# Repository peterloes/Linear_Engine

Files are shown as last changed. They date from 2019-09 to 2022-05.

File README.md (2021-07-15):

# Linear Actuator

A standalone Platform for Animal Manipulation 

This is the firmware for the LinearA_2017 (linear servo, i.e. stepper motor with spindle)
and project Servo_2015 (standard PWM servo).
Setup and control of the Actuator is done
via 3 keys, and, for selecting the two end positions, also via two external
inputs, please see below.  The firmware supports soft-start, i.e. the Actuator
speed will be ramped-up during the start phase.

Supported:
- Nanotec SMC11-2 Leistungsendstufe
- Nanotec Linear Aktuator L2018S0604-T3,5x1

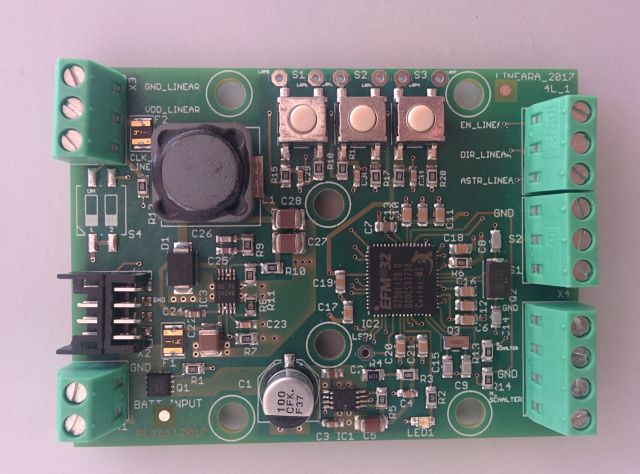
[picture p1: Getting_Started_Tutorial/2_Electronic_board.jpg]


The linear setup procedure consists of 4 steps:
- Adjust end position 1.  A linear actuator
  doesn't know about its absolute position, therefore it first moves to
  to its physical start position (near the motor) after power-up.  From
  that, position 1 can be adjusted.
- Adjust end position 2.  This is the opposite end position to position 1.
- Adjust actuator speed.  The actuator permanently moves between the two end
  points.  The speed can be adjusted via S1 and S2.
- Asserting S3 the 4th time stores the servo parameters into FLASH and
  returns to normal operation.

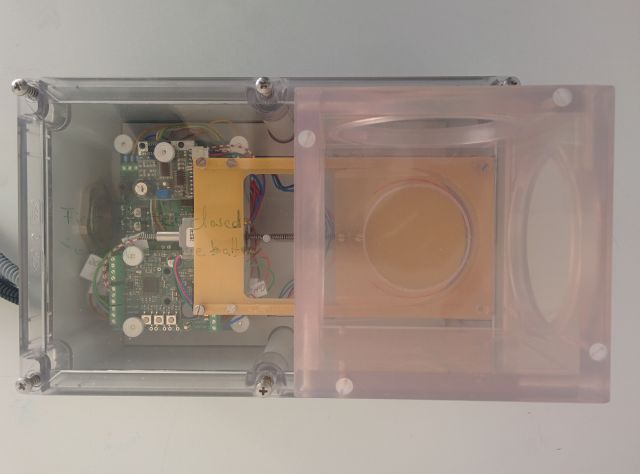
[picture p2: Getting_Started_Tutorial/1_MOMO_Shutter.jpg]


Prototype: Feeder

https://github.com/peterloes/Linear_Engine/blob/master/Getting_Started_Tutorial/1_poster_overview.pdf

Mainboard:

https://github.com/peterloes/MOMO

Manufacture:

https://github.com/peterloes/Linear_Engine/blob/master/Getting_Started_Tutorial/3_Supplier.txt

The standalone Linear Actuator features EFM32 ...the world´s most energy friendly microcontrollers

ARM Cortex-M3 EFM32G230F128

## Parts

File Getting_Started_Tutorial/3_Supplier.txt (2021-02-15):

Linear Actuator & Power Output Stage

L2018S0604-T3,5X1 Linearaktuator 
SMC11-2 Mikroschritt Leistungsendstufe
ZK-SMC11 Anschlusskabel
ZST3,5-1200-1 

Nanotec Electronic GmbH & Co. KG
Kapellenstr. 6
D-85622 Feldkirchen b. München 

Telefon: ++49-89-900686-0
Fax:     ++49-89-900686-50
Email:   info@nanotec.de
http://www.nanotec.de

Supplier of all Electronic Boards

Top-Print Electronic GmbH
Oskar Schmid

Rosenheimer Landstr. 129a
85521 Ottobrunn
Germany
Tel.: +49-89-60668047
Fax: +49-89-60668049
mailto: info@top-print.eu
https://www.leiterplatten-muenchen.de/

Protective coating with Schmelzharz Bectron MR3404

KC – Kunststoff- Chemische Produkte GmbH
Holger Sarau-Burghardt

Leonberger Straße 86 
DE 71292 Friolzheim
phone: +49 (0)7044 9425 13
e-mail: h.sarau-burghardt@kc-produkte.com
http: www.conformalcoating.de

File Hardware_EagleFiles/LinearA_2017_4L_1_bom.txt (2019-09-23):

Part  Value                Device                  Package                Description                                                    MF MPN OC_FARNELL OC_NEWARK
C1    100µ/16V             CPOL-EUE                PANASONIC_E            POLARIZED CAPACITOR, European symbol                                                      
C2    1uF                  C-EUC0603               C0603                  CAPACITOR, European symbol                                                                
C3    1nF                  C-EUC0603               C0603                  CAPACITOR, European symbol                                                                
C4    10nF                 C-EUC0603               C0603                  CAPACITOR, European symbol                                                                
C5    10uF                 C-EUC1206               C1206                  CAPACITOR, European symbol                                                                
C6    100n                 C_SMD0805               0805                                                                                                             
C7    1u                   C_SMD0805               0805                                                                                                             
C8    12p                  C_SMD0805               0805                                                                                                             
C9    18p                  C_SMD0805               0805                                                                                                             
C10   100n                 C_SMD0805               0805                                                                                                             
C11   100n                 C_SMD0805               0805                                                                                                             
C12   100n                 C_SMD0805               0805                                                                                                             
C13   100n                 C_SMD0805               0805                                                                                                             
C14   12p                  C_SMD0805               0805                                                                                                             
C15   18p                  C_SMD0805               0805                                                                                                             
C16   100n                 C_SMD0805               0805                                                                                                             
C17   100n                 C_SMD0805               0805                                                                                                             
C18   100n                 C_SMD0805               0805                                                                                                             
C19   100n                 C_SMD0805               0805                                                                                                             
C20   100n                 C_SMD0805               0805                                                                                                             
C21   100n                 C_SMD0805               0805                                                                                                             
C22   4.7µF                C-EUC1210               C1210                  CAPACITOR, European symbol                                                                
C23   10nF                 C-EUC0603               C0603                  CAPACITOR, European symbol                                                                
C24   100nF                C-EUC0603               C0603                  CAPACITOR, European symbol                                                                
C25   4.3nF                C-EUC0603               C0603                  CAPACITOR, European symbol                                                                
C26   24pF                 C-EUC0603               C0603                  CAPACITOR, European symbol                                                                
C27   22µF                 C-EUC1210               C1210                  CAPACITOR, European symbol                                                                
C28   22µF                 C-EUC1210               C1210                  CAPACITOR, European symbol                                                                
C29   10n                  C-EUC0603               C0603                  CAPACITOR, European symbol                                                                
C30   10n                  C-EUC0603               C0603                  CAPACITOR, European symbol                                                                
C31   10n                  C-EUC0603               C0603                  CAPACITOR, European symbol                                                                
D1    B360B                SCHOTTKY-DIODESMD       SMB                    Schottky Diode                                                                            
F1    MF-USMF050           PFUF                    PFUF_1210POLY                                                                                                    
F2    MF-USMF050           PFUF                    PFUF_1210POLY                                                                                                    
IC1   TPS7A1601DGNT        TPS7A16                 DGN_S-PDSO-G8-EXP                                                                                                
IC2   EFM32G230F128        EFM32G230F128           QFN64                  EFM32G230F128 Gecko Microcontroller in 9mm x 9mm QFN64 package                            
IC3   TPS54240DGQR         TPS54240DGQR            S-PDSO-G10                                                                                                       
L1    PIS4728-220M-04      DR127                   DR127                  High Power Density, High Efficiency, Shielded Inductors                                   
LED1  SML-H12U8TT86        LEDCHIPLED_0805         CHIPLED_0805           LED                                                                                       
LSP1  (n.b.)LSP10          LSP10                   LSP10                  SOLDER PAD drill 1.0 mm, distributor Buerklin, 12H555                                     
LSP2  (n.b.)LSP10          LSP10                   LSP10                  SOLDER PAD drill 1.0 mm, distributor Buerklin, 12H555                                     
LSP3  (n.b.)LSP10          LSP10                   LSP10                  SOLDER PAD drill 1.0 mm, distributor Buerklin, 12H555                                     
LSP4  (n.b.)LSP10          LSP10                   LSP10                  SOLDER PAD drill 1.0 mm, distributor Buerklin, 12H555                                     
LSP5  (n.b.)LSP10          LSP10                   LSP10                  SOLDER PAD drill 1.0 mm, distributor Buerklin, 12H555                                     
LSP6  (n.b.)LSP10          LSP10                   LSP10                  SOLDER PAD drill 1.0 mm, distributor Buerklin, 12H555                                     
LSP7  (n.b.)LSP10          LSP10                   LSP10                  SOLDER PAD drill 1.0 mm, distributor Buerklin, 12H555                                     
PASS1 ROUND_1MM1.5         ROUND_1MM1.5            ROUND2_1.5MM                                                                                                     
PASS2 ROUND_1MM1.5         ROUND_1MM1.5            ROUND2_1.5MM                                                                                                     
Q1    SI7121DN             TRANSISTOR-FET_SI7113DN TRANSISTOR-FET_1212-8S                                                                                           
Q2    NX5032GA/32MHz/8pF   CRYSTAL2P5.0X3.2        CRYSTAL2P5.0X3.2       Quarz Crystal                                                                             
Q3    CM7V, 32768Hz/12.5pF CRYSTAL2P               CRYSTAL2P3.2X1.5       Quarz Crystal                                                                             
R1    100k                 R-EU_R0805              R0805                  RESISTOR, European symbol                                                                 
R2    1K2                  R-EU_R0805              R0805                  RESISTOR, European symbol                                                                 
R3    2M                   R-EU_R0805              R0805                  RESISTOR, European symbol                                                                 
R4    1M13                 R-EU_R0805              R0805                  RESISTOR, European symbol                                                                 
R5    100K                 R-EU_R0805              R0805                  RESISTOR, European symbol                                                                 
R6    1                    R-EU_R0805              R0805                  RESISTOR, European symbol                                                                 
R7    100K                 R-EU_R0805              R0805                  RESISTOR, European symbol                                                                 
R8    348K                 R-EU_R0805              R0805                  RESISTOR, European symbol                                                                 
R9    39K                  R-EU_R0805              R0805                  RESISTOR, European symbol                                                                 
R10   140K                 R-EU_R0805              R0805                  RESISTOR, European symbol                                                                 
R11   10k                  R-EU_R0805              R0805                  RESISTOR, European symbol                                                                 
R12   100                  R-EU_R0805              R0805                  RESISTOR, European symbol                                                                 
R13   1K                   R-EU_R0805              R0805                  RESISTOR, European symbol                                                                 
R14   1K                   R-EU_R0805              R0805                  RESISTOR, European symbol                                                                 
R15   100K                 R-EU_R0805              R0805                  RESISTOR, European symbol                                                                 
R16   100K                 R-EU_R0805              R0805                  RESISTOR, European symbol                                                                 
R17   100K                 R-EU_R0805              R0805                  RESISTOR, European symbol                                                                 
R18   100                  R-EU_R0805              R0805                  RESISTOR, European symbol                                                                 
R19   100                  R-EU_R0805              R0805                  RESISTOR, European symbol                                                                 
R20   100                  R-EU_R0805              R0805                  RESISTOR, European symbol                                                                 
S1    SWPB_B3S1000         DTSM-6                  DTSM-6                                                                                                           
S2    SWPB_B3S1000         DTSM-6                  DTSM-6                                                                                                           
S3    SWPB_B3S1000         DTSM-6                  DTSM-6                                                                                                           
S4    (n.b.)SBS9102TK      219-02                  CTS-219-02             Surface Mount DIP Switch Series 219 SMT                               unknown    unknown  
X1    MKDS1/2-3,81         MKDS1/2-3,81            2POL381                MKDS 1/2-3,81 - Order No. 1727010 (RS-Online - 101-5384)                                  
X2    DP11_8DP_2DS         DP11_8DP_2DS            DP11_8DP-2DS                                                                                                     
X3    MKDS1/3-3,81         MKDS1/3-3,81            3POL381                MKDS 1/3-3,81 - Order No. 1727023 (RS-Online - 101-5390)                                  
X4    MKDS1/3-3,81         MKDS1/3-3,81            3POL381                MKDS 1/3-3,81 - Order No. 1727023 (RS-Online - 101-5390)                                  
X5    MKDS1/3-3,81         MKDS1/3-3,81            3POL381                MKDS 1/3-3,81 - Order No. 1727023 (RS-Online - 101-5390)                                  
X6    MKDS1/4-3,81         MKDS1/4-3,81            4POL381                MKDS 1/4-3,81 - Order No. 1727036

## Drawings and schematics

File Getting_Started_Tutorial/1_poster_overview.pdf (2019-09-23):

# Linear actuator and servomotor

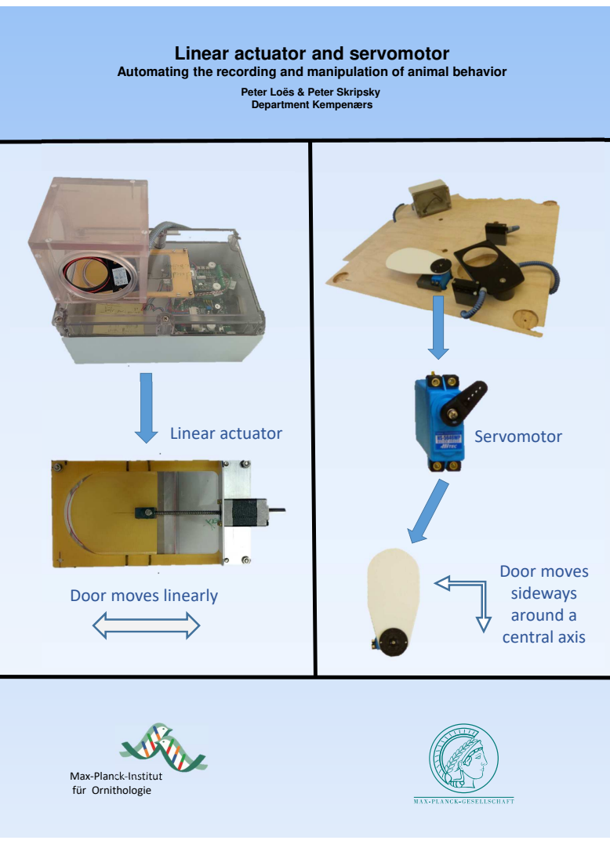
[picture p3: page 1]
Servomotor; Door moves sideways around a central axis; Linear actuator

Automating the recording and manipulation of animal behavior

Peter Loës & Peter Skripsky
Department Kempenærs

Door moves linearly

Max-Planck-Institut
für Ornithologie

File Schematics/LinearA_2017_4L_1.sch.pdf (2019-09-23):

### Wide Input Voltage Range: 12V to 35V VDD_LINEAR 9V - max. 35V

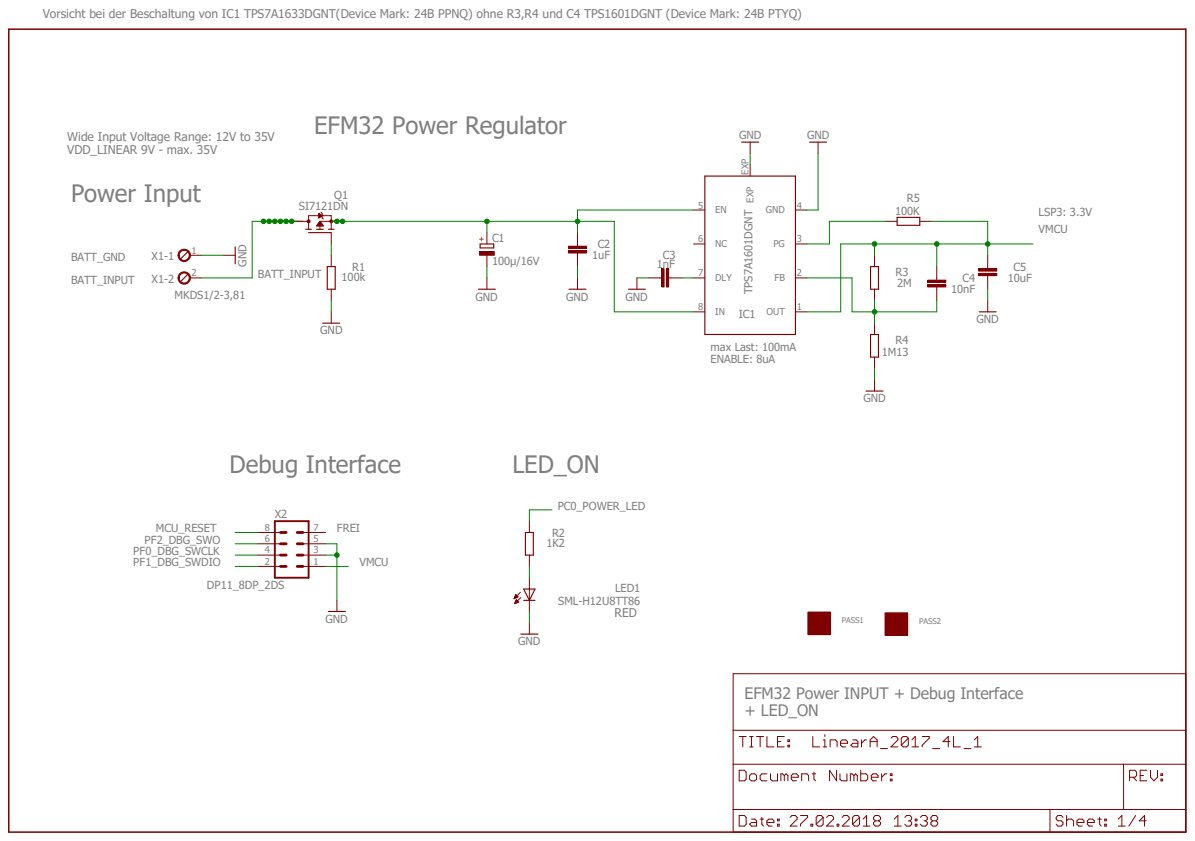
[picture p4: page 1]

Vorsicht bei der Beschaltung von IC1 TPS7A1633DGNT(Device Mark: 24B PPNQ) ohne R3,R4 und C4 TPS1601DGNT (Device Mark: 24B PTYQ)

EFM32 Power INPUT + Debug Interface
+ LED_ON

# EFM32 I/O + POWER

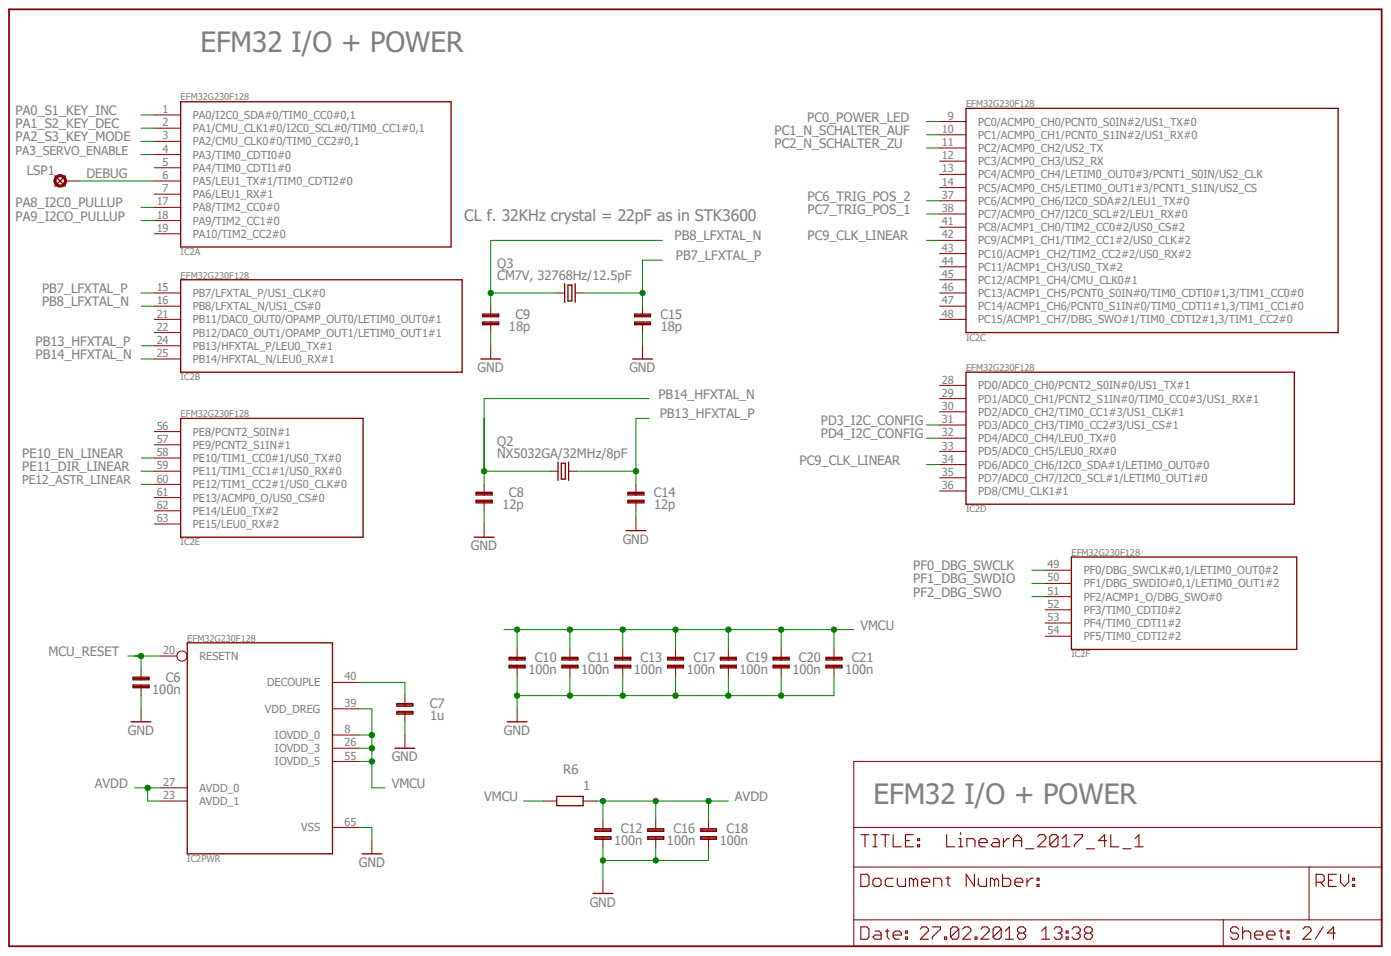
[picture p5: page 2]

CL f. 32KHz crystal = 22pF as in STK3600

## 11V_Ausgabe

# POWER OUTPUTs

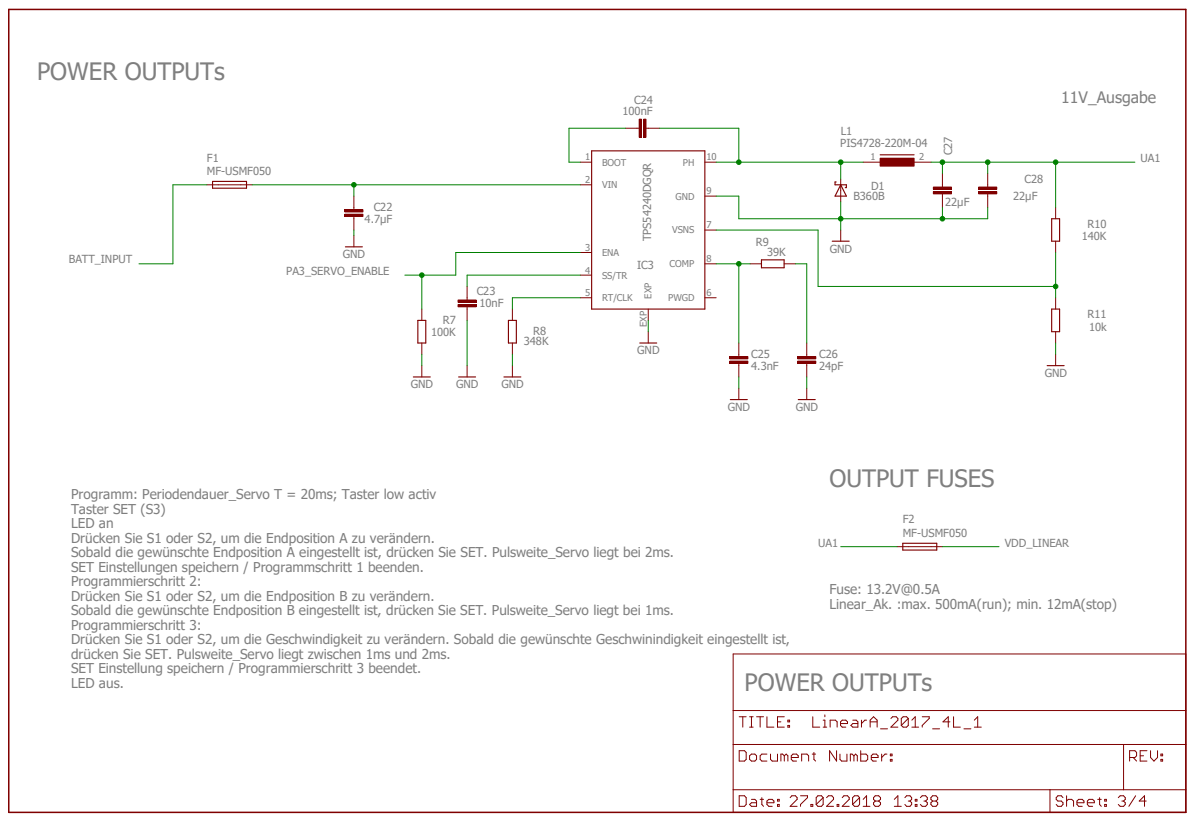
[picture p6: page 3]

Programm: Periodendauer_Servo T = 20ms; Taster low activ
Taster SET (S3)
LED an
Drücken Sie S1 oder S2, um die Endposition A zu verändern.
Sobald die gewünschte Endposition A eingestellt ist, drücken Sie SET. Pulsweite_Servo liegt bei 2ms.
SET Einstellungen speichern / Programmschritt 1 beenden.
Programmierschritt 2:
Drücken Sie S1 oder S2, um die Endposition B zu verändern.
Sobald die gewünschte Endposition B eingestellt ist, drücken Sie SET. Pulsweite_Servo liegt bei 1ms.
Programmierschritt 3:
Drücken Sie S1 oder S2, um die Geschwindigkeit zu verändern. Sobald die gewünschte Geschwinindigkeit eingestellt ist,
drücken Sie SET. Pulsweite_Servo liegt zwischen 1ms und 2ms.
SET Einstellung speichern / Programmierschritt 3 beendet.
LED aus.

Fuse: 13.2V@0.5A
Linear_Ak. :max. 500mA(run); min. 12mA(stop)

# LINEAR

## SMC11_Nanotec

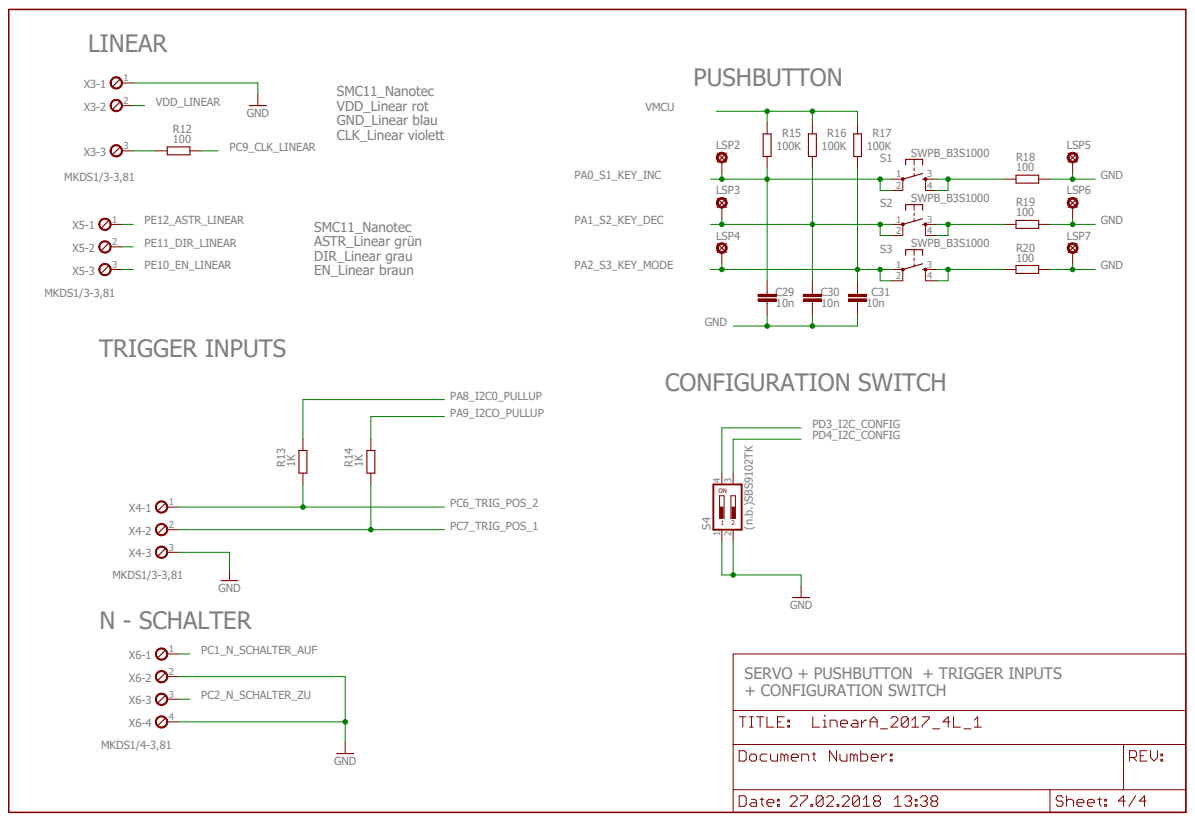
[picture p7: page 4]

SERVO + PUSHBUTTON + TRIGGER INPUTS
+ CONFIGURATION SWITCH

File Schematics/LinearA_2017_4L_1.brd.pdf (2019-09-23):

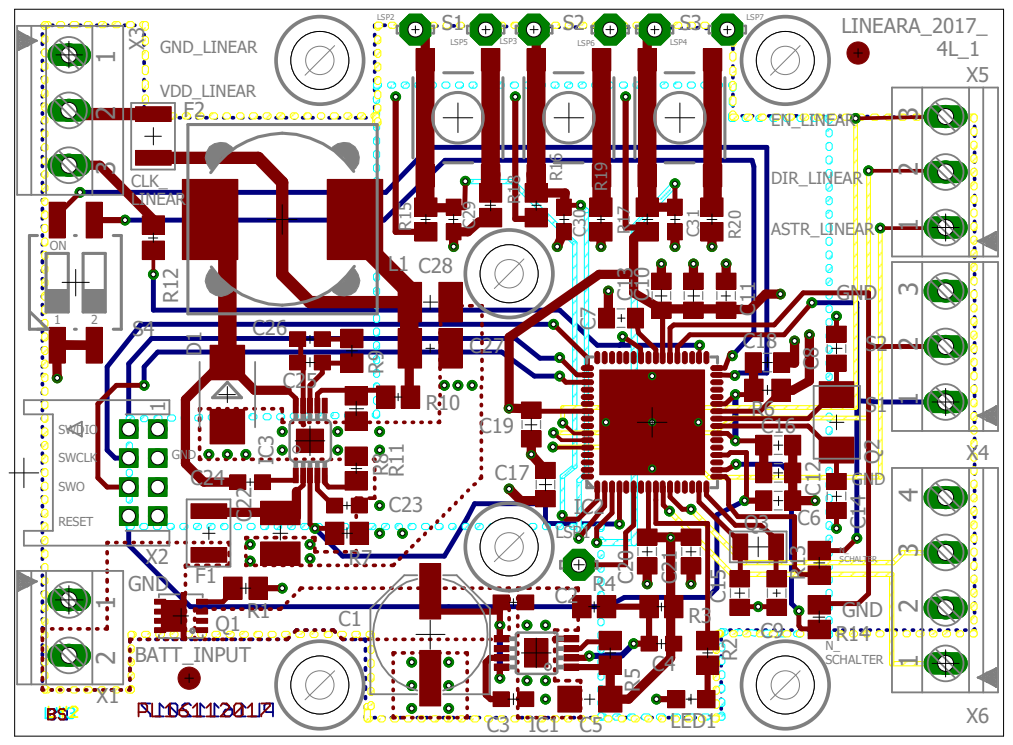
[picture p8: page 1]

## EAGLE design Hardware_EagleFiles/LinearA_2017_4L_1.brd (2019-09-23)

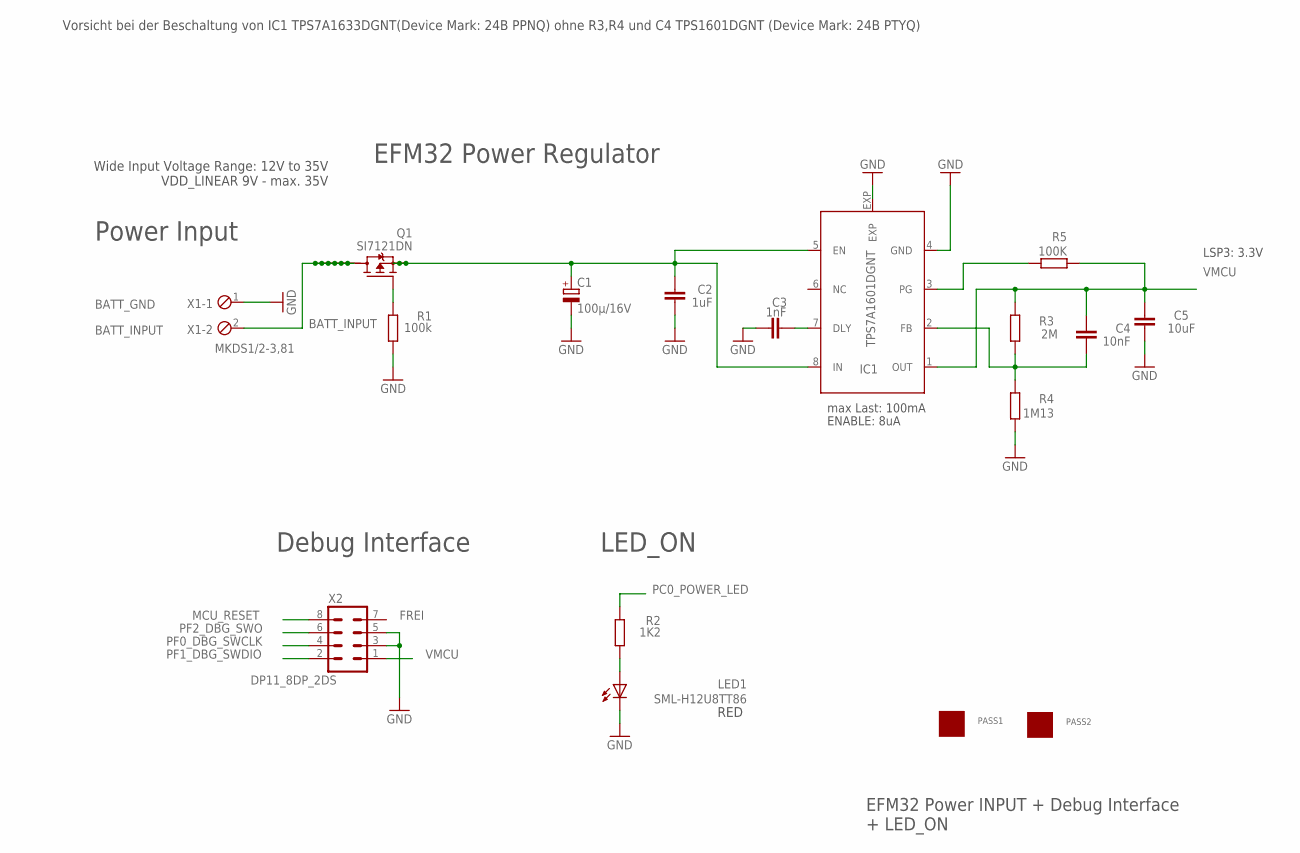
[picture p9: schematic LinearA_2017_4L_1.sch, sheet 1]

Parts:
C1: 100µ/16V; PANASONIC_E
C2: 1uF; C0603
C3: 1nF; C0603
C4: 10nF; C0603
C5: 10uF; C1206
IC1: TPS7A1601DGNT; DGN_S-PDSO-G8-EXP
LED1: SML-H12U8TT86; CHIPLED_0805
PASS1, PASS2: ROUND_1MM1.5; ROUND2_1.5MM
Q1: SI7121DN; TRANSISTOR-FET_1212-8S
R1: 100k; R0805
R2: 1K2; R0805
R3: 2M; R0805
R4: 1M13; R0805
R5: 100K; R0805
X1: MKDS1/2-3,81; 2POL381
X2: DP11_8DP_2DS; DP11_8DP-2DS

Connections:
BATT_INPUT: Q1.5 (D), Q1.6 (D), Q1.7 (D), Q1.8 (D), Q1.9 (D), Q1.10 (D), Q1.11 (D), X1.2; also elsewhere on the board
GND: C1.-, C2.1, C3.1, C5.1, IC1.4 (GND), IC1.EXP, LED1.C, R1.1, R4.1, X1.1, X2.3, X2.5; also elsewhere on the board
MCU_RESET: X2.8; also elsewhere on the board
unnamed: C1.+, C2.2, IC1.5 (EN), IC1.8 (IN), Q1.1 (S), Q1.2 (S), Q1.3 (S)
unnamed: C3.2, IC1.7 (DLY)
unnamed: C4.1, IC1.2 (FB), R3.1, R4.2
unnamed: IC1.3 (PG), R5.2
unnamed: Q1.4 (G), R1.2
unnamed: LED1.A, R2.2
PC0_POWER_LED: R2.1; also elsewhere on the board
PF0_DBG_SWCLK: X2.4; also elsewhere on the board
PF1_DBG_SWDIO: X2.2; also elsewhere on the board
PF2_DBG_SWO: X2.6; also elsewhere on the board
VMCU: C4.2, C5.2, IC1.1 (OUT), R3.2, R5.1, X2.1; also elsewhere on the board

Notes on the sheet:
BATT_GND
Wide Input Voltage Range: 12V to 35V VDD_LINEAR 9V - max. 35V
BATT_INPUT
EFM32 Power INPUT + Debug Interface + LED_ON
ENABLE: 8uA
Power Input
max Last: 100mA
LSP3: 3.3V
EFM32 Power Regulator
Debug Interface
LED_ON
FREI
Vorsicht bei der Beschaltung von IC1 TPS7A1633DGNT(Device Mark: 24B PPNQ) ohne R3,R4 und C4 TPS1601DGNT (Device Mark: 24B PTYQ)
RED

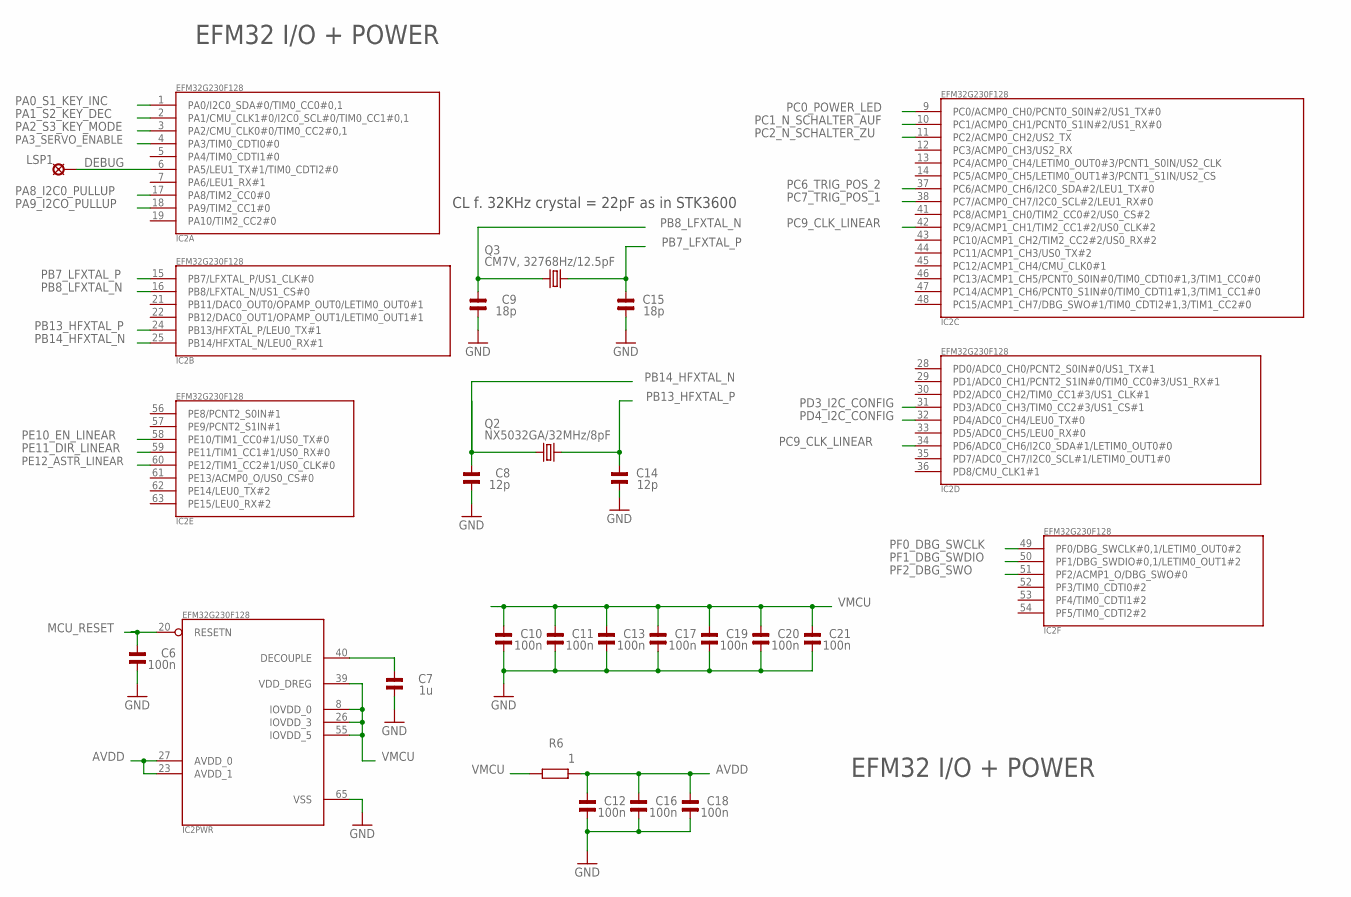
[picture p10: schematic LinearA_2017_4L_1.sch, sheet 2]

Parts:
C6, C10, C11, C12, C13, C16, C17, C18, C19, C20, C21: 100n; 0805
C7: 1u; 0805
C8, C14: 12p; 0805
C9, C15: 18p; 0805
IC2: EFM32G230F128; QFN64
LSP1: (n.b.)LSP10; LSP10
Q2: NX5032GA/32MHz/8pF; CRYSTAL2P5.0X3.2
Q3: CM7V, 32768Hz/12.5pF; CRYSTAL2P3.2X1.5
R6: 1; R0805

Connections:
AVDD: C12.2, C16.2, C18.2, IC2.23 (AVDD_1), IC2.27 (AVDD_0), R6.2
DEBUG: IC2.6 (PA5/LEU1_TX#1/TIM0_CDTI2#0), LSP1.MP
GND: C6.1, C7.1, C8.1, C9.1, C10.1, C11.1, C12.1, C13.1, C14.1, C15.1, C16.1, C17.1, C18.1, C19.1, C20.1, C21.1, IC2.65 (VSS); also elsewhere on the board
MCU_RESET: C6.2, IC2.20 (RESETN); also elsewhere on the board
unnamed: C7.2, IC2.40 (DECOUPLE)
PA0_S1_KEY_INC: IC2.1 (PA0/I2C0_SDA#0/TIM0_CC0#0,1); also elsewhere on the board
PA1_S2_KEY_DEC: IC2.2 (PA1/CMU_CLK1#0/I2C0_SCL#0/TIM0_CC1#0,1); also elsewhere on the board
PA2_S3_KEY_MODE: IC2.3 (PA2/CMU_CLK0#0/TIM0_CC2#0,1); also elsewhere on the board
PA3_SERVO_ENABLE: IC2.4 (PA3/TIM0_CDTI0#0); also elsewhere on the board
PA8_I2C0_PULLUP: IC2.17 (PA8/TIM2_CC0#0); also elsewhere on the board
PA9_I2CO_PULLUP: IC2.18 (PA9/TIM2_CC1#0); also elsewhere on the board
PB7_LFXTAL_P: C15.2, IC2.15 (PB7/LFXTAL_P/US1_CLK#0), Q3.2
PB8_LFXTAL_N: C9.2, IC2.16 (PB8/LFXTAL_N/US1_CS#0), Q3.1
PB13_HFXTAL_P: C14.2, IC2.24 (PB13/HFXTAL_P/LEU0_TX#1), Q2.2
PB14_HFXTAL_N: C8.2, IC2.25 (PB14/HFXTAL_N/LEU0_RX#1), Q2.1
PC0_POWER_LED: IC2.9 (PC0/ACMP0_CH0/PCNT0_S0IN#2/US1_TX#0); also elsewhere on the board
PC1_N_SCHALTER_AUF: IC2.10 (PC1/ACMP0_CH1/PCNT0_S1IN#2/US1_RX#0); also elsewhere on the board
PC2_N_SCHALTER_ZU: IC2.11 (PC2/ACMP0_CH2/US2_TX); also elsewhere on the board
PC6_TRIG_POS_2: IC2.37 (PC6/ACMP0_CH6/I2C0_SDA#2/LEU1_TX#0); also elsewhere on the board
PC7_TRIG_POS_1: IC2.38 (PC7/ACMP0_CH7/I2C0_SCL#2/LEU1_RX#0); also elsewhere on the board
PC9_CLK_LINEAR: IC2.34 (PD6/ADC0_CH6/I2C0_SDA#1/LETIM0_OUT0#0), IC2.42 (PC9/ACMP1_CH1/TIM2_CC1#2/US0_CLK#2); also elsewhere on the board
PD3_I2C_CONFIG: IC2.31 (PD3/ADC0_CH3/TIM0_CC2#3/US1_CS#1); also elsewhere on the board
PD4_I2C_CONFIG: IC2.32 (PD4/ADC0_CH4/LEU0_TX#0); also elsewhere on the board
PE10_EN_LINEAR: IC2.58 (PE10/TIM1_CC0#1/US0_TX#0); also elsewhere on the board
PE11_DIR_LINEAR: IC2.59 (PE11/TIM1_CC1#1/US0_RX#0); also elsewhere on the board
PE12_ASTR_LINEAR: IC2.60 (PE12/TIM1_CC2#1/US0_CLK#0); also elsewhere on the board
PF0_DBG_SWCLK: IC2.49 (PF0/DBG_SWCLK#0,1/LETIM0_OUT0#2); also elsewhere on the board
PF1_DBG_SWDIO: IC2.50 (PF1/DBG_SWDIO#0,1/LETIM0_OUT1#2); also elsewhere on the board
PF2_DBG_SWO: IC2.51 (PF2/ACMP1_O/DBG_SWO#0); also elsewhere on the board
VMCU: C10.2, C11.2, C13.2, C17.2, C19.2, C20.2, C21.2, IC2.8 (IOVDD_0), IC2.26 (IOVDD_3), IC2.39 (VDD_DREG), IC2.55 (IOVDD_5), R6.1; also elsewhere on the board

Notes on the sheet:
EFM32 I/O + POWER
CL f. 32KHz crystal = 22pF as in STK3600

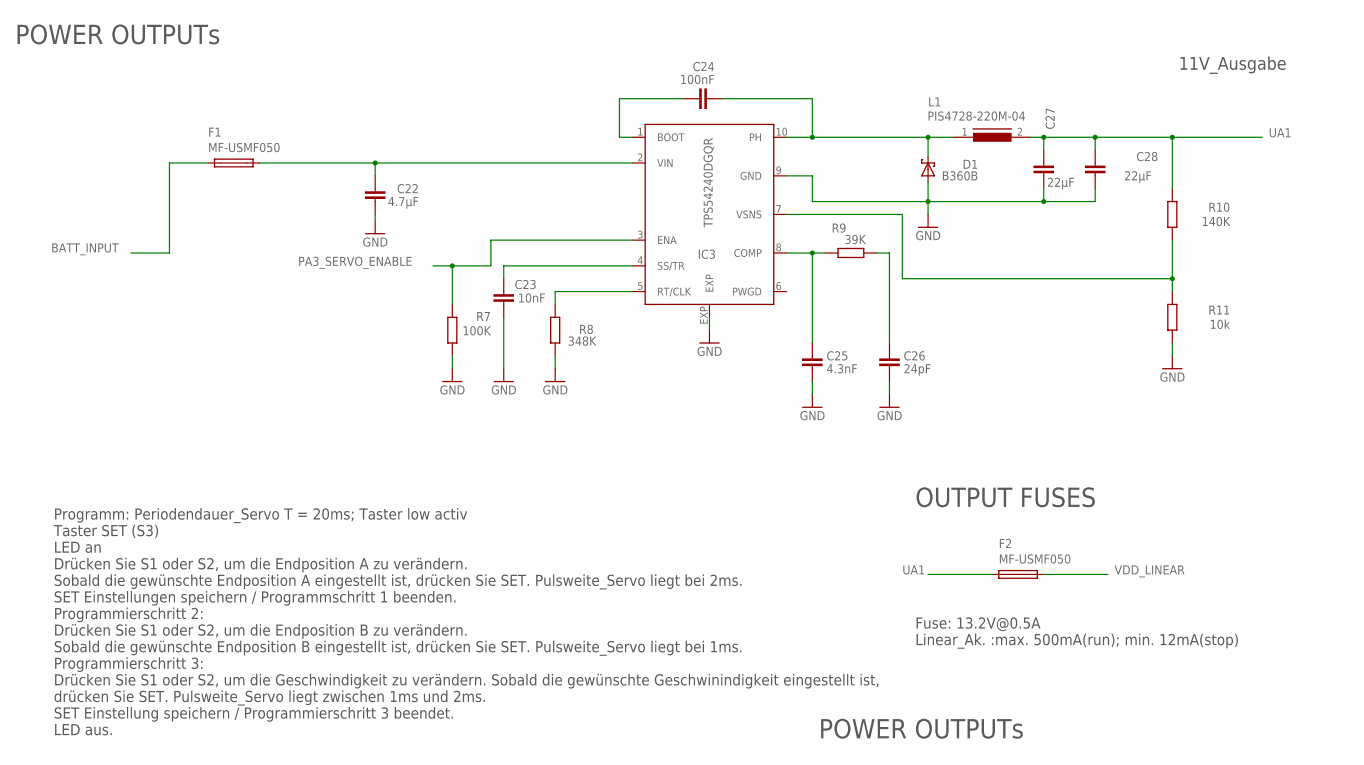
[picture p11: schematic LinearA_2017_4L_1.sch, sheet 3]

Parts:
C22: 4.7µF; C1210
C23: 10nF; C0603
C24: 100nF; C0603
C25: 4.3nF; C0603
C26: 24pF; C0603
C27, C28: 22µF; C1210
D1: B360B; SMB
F1, F2: MF-USMF050; PFUF_1210POLY
IC3: TPS54240DGQR; S-PDSO-G10
L1: PIS4728-220M-04; DR127
R7: 100K; R0805
R8: 348K; R0805
R9: 39K; R0805
R10: 140K; R0805
R11: 10k; R0805

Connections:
BATT_INPUT: F1.P$1 (1); also elsewhere on the board
GND: C22.2, C23.2, C25.2, C26.2, C27.2, C28.2, D1.A, IC3.9 (GND), IC3.EXP, R7.1, R8.1, R11.1; also elsewhere on the board
unnamed: IC3.5 (RT/CLK), R8.2
unnamed: C24.2, IC3.1 (BOOT)
unnamed: C24.1, D1.C, IC3.10 (PH), L1.1
unnamed: C23.1, IC3.4 (SS/TR)
unnamed: C25.1, IC3.8 (COMP), R9.1
unnamed: C26.1, R9.2
unnamed: IC3.7 (VSNS), R10.1, R11.2
unnamed: C22.1, F1.P$2 (2), IC3.2 (VIN)
PA3_SERVO_ENABLE: IC3.3 (ENA), R7.2; also elsewhere on the board
UA1: C27.1, C28.1, F2.P$1 (1), L1.2, R10.2
VDD_LINEAR: F2.P$2 (2); also elsewhere on the board

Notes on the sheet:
11V_Ausgabe
POWER OUTPUTs
OUTPUT FUSES
Programm: Periodendauer_Servo T = 20ms; Taster low activ Taster SET (S3) LED an Drücken Sie S1 oder S2, um die Endposition A zu verändern. Sobald die gewünschte Endposition A eingestellt ist, drücken Sie SET. Pulsweite_Servo liegt bei 2ms. SET Einstellungen speichern / Programmschritt 1 beenden. Pr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
Fuse: 13.2V@0.5A Linear_Ak. :max. 500mA(run); min. 12mA(stop)

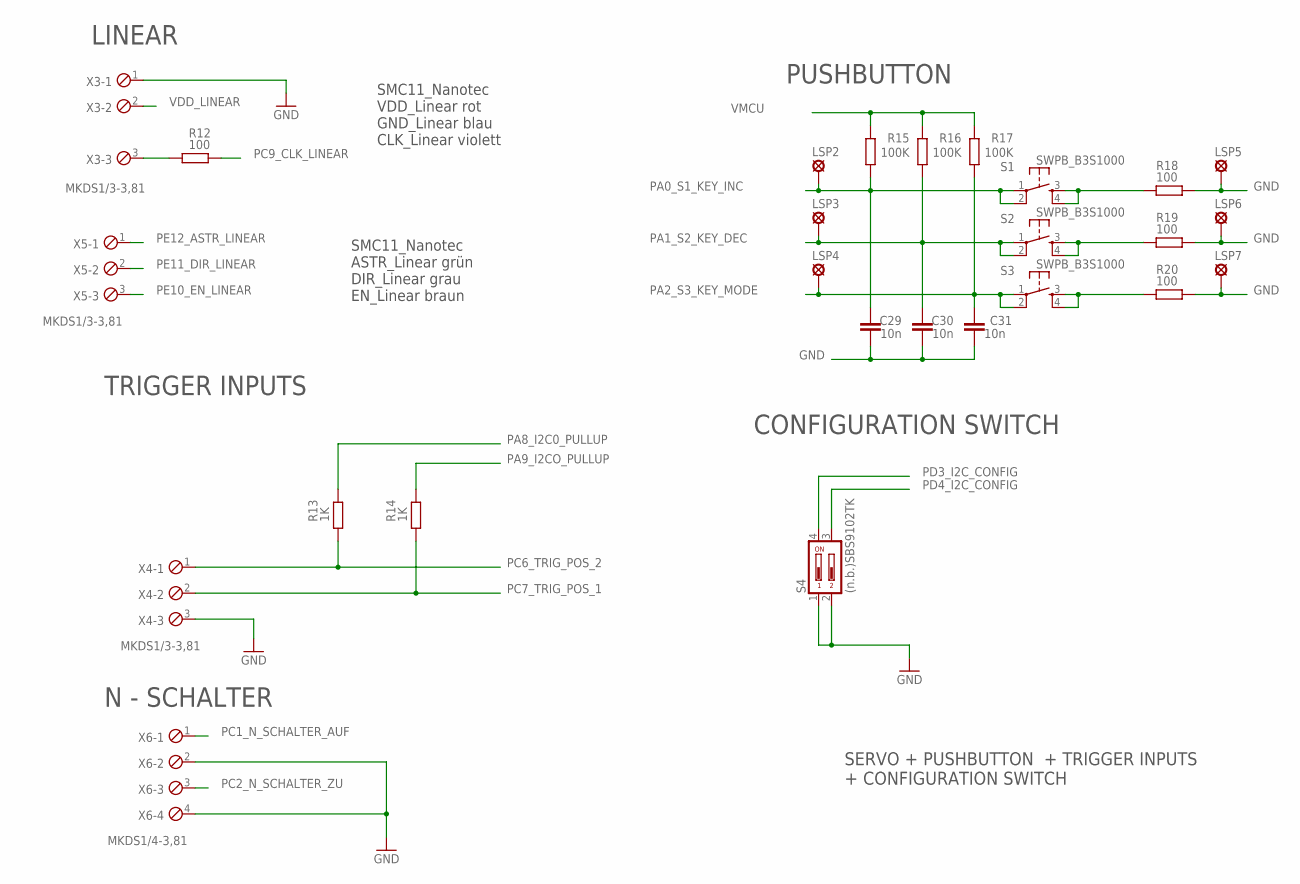
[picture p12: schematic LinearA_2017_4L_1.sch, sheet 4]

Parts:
C29, C30, C31: 10n; C0603
LSP2, LSP3, LSP4, LSP5, LSP6, LSP7: (n.b.)LSP10; LSP10
R12, R18, R19, R20: 100; R0805
R13, R14: 1K; R0805
R15, R16, R17: 100K; R0805
S1, S2, S3: SWPB_B3S1000; DTSM-6
S4: (n.b.)SBS9102TK; CTS-219-02
X3, X4, X5: MKDS1/3-3,81; 3POL381
X6: MKDS1/4-3,81; 4POL381

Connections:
GND: C29.1, C30.1, C31.1, LSP5.MP, LSP6.MP, LSP7.MP, R18.2, R19.2, R20.2, S4.1, S4.2, X3.1, X4.3, X6.2, X6.4; also elsewhere on the board
unnamed: R12.1, X3.3
unnamed: R20.1, S3.3, S3.4
unnamed: R18.1, S1.3, S1.4
unnamed: R19.1, S2.3, S2.4
PA0_S1_KEY_INC: C29.2, LSP2.MP, R15.1, S1.1, S1.2; also elsewhere on the board
PA1_S2_KEY_DEC: C30.2, LSP3.MP, R16.1, S2.1, S2.2; also elsewhere on the board
PA2_S3_KEY_MODE: C31.2, LSP4.MP, R17.1, S3.1, S3.2; also elsewhere on the board
PA8_I2C0_PULLUP: R13.2; also elsewhere on the board
PA9_I2CO_PULLUP: R14.2; also elsewhere on the board
PC1_N_SCHALTER_AUF: X6.1; also elsewhere on the board
PC2_N_SCHALTER_ZU: X6.3; also elsewhere on the board
PC6_TRIG_POS_2: R13.1, X4.1; also elsewhere on the board
PC7_TRIG_POS_1: R14.1, X4.2; also elsewhere on the board
PC9_CLK_LINEAR: R12.2; also elsewhere on the board
PD3_I2C_CONFIG: S4.4; also elsewhere on the board
PD4_I2C_CONFIG: S4.3; also elsewhere on the board
PE10_EN_LINEAR: X5.3; also elsewhere on the board
PE11_DIR_LINEAR: X5.2; also elsewhere on the board
PE12_ASTR_LINEAR: X5.1; also elsewhere on the board
VDD_LINEAR: X3.2; also elsewhere on the board
VMCU: R15.2, R16.2, R17.2; also elsewhere on the board

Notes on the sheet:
SERVO + PUSHBUTTON + TRIGGER INPUTS + CONFIGURATION SWITCH
LINEAR
SMC11_Nanotec VDD_Linear rot GND_Linear blau CLK_Linear violett
TRIGGER INPUTS
PUSHBUTTON
CONFIGURATION SWITCH
SMC11_Nanotec ASTR_Linear grün DIR_Linear grau EN_Linear braun
N - SCHALTER

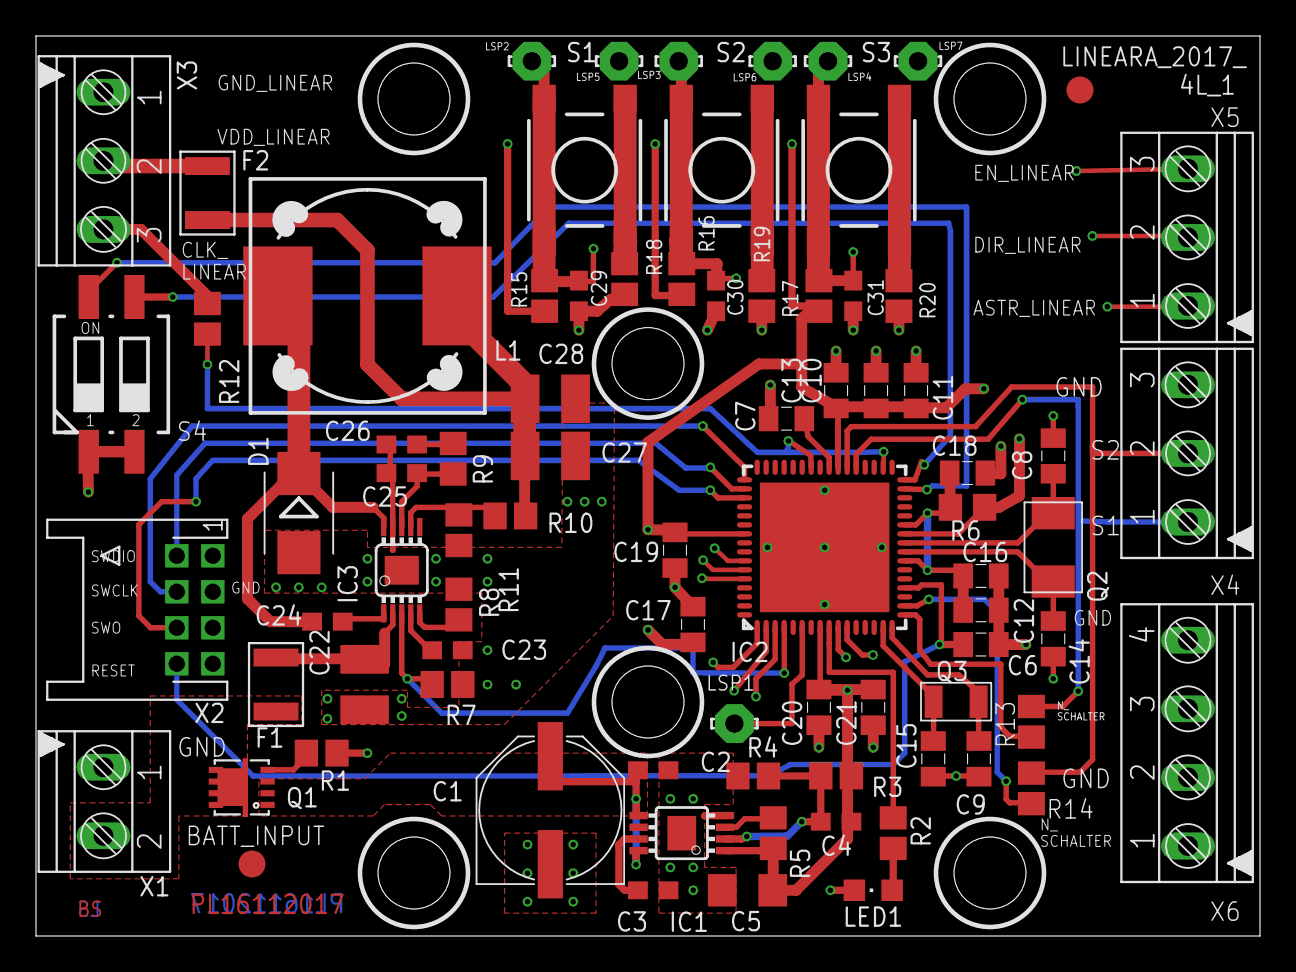
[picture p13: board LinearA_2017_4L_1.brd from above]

Board: 4 copper layers, 68.0 x 50.0 mm, 81 parts (0 on the bottom side), 51 nets.

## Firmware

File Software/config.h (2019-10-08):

/***************************************************************************//**
 * @file
 * @brief	Project configuration file
 * @author	Ralf Gerhauser
 * @version	2016-10-05
 *
 * This file allows to set miscellaneous configuration parameters.  It must be
 * included by all modules.
 *
 ****************************************************************************//*
Revision History:
2017-07-01,rage	Added configuration CFG_LINEAR_A.
2016-09-09,rage	Derived from project "SNB_Heaven".
*/

#ifndef __INC_config_h
#define __INC_config_h

/*=============================== Header Files ===============================*/

#include <stdio.h>
#include <stdbool.h>
#include "em_device.h"

/*=============================== Definitions ================================*/

/*
 * Basic defines - should all be moved to Generic.h
 */
    /* terminators for lists and strings */

#define	EOL		NULL		/* EndOfList		*/
#define EOS		'\0'		/* EndOfString		*/
#define	NONE		(-1)

    /* macro to calculate the number of elements of an array */
#define ELEM_CNT(array)  (sizeof (array) / sizeof ((array)[0]))


/*!
 * @brief Select hardware platform for this firmware.
 * If CFG_LINEAR_A is 1, the firmware supports the SMC11 stepper module
 * (file LinearA.c), if 0, a standard PWM servo (file Servo.c) is supported.
 */
#define CFG_LINEAR_A	1

/*
 * LED Definitions for this project
 */
    /*!@brief GPIO Port of the (red) Power-LED. */
#define POWER_LED_PORT		gpioPortC
    /*!@brief GPIO Pin of the (red) Power-LED. */
#define POWER_LED_PIN		0
    /*! @brief Macro to set or clear the Power-LED */
#define POWER_LED   IO_Bit(GPIO->P[POWER_LED_PORT].DOUT, POWER_LED_PIN)

/*!
 * @brief MPU Clock Configuration.
 *
 * Set to 0 to use the internal RC oscillator, if 1 the external 32MHz XTAL
 * is used - must be set 1 for this project.
 */
#define USE_EXT_32MHZ_CLOCK	1

/*
 * Configuration for module "AlarmClock"
 */
    /*!@brief RTC frequency in [Hz]. */
#define RTC_COUNTS_PER_SEC	32768


/*================================== Macros ==================================*/

#ifdef DEBUG
    /*
     * Debugging output via ITM
     */
    #define DBG_PUTC(ch)	ITM_SendChar(ch)
    #define DBG_PUTS(str)	ITM_SendStr(str)
    uint32_t ITM_SendChar (uint32_t ch);
    void ITM_SendStr(const char *pStr);
    void dbgInit(void);
#else
    #define DBG_PUTC(ch)
    #define DBG_PUTS(str)
#endif

    /*! Macro to address a single bit in the I/O range (peripheral range) in
     *  an atomic manner.
     * @param address   I/O register address.
     * @param bitNum    Bit number within this register.
     */
#define IO_BIT_ADDR(address, bitNum)					\
	((__IO uint32_t *) (BITBAND_PER_BASE				\
			+ (((uint32_t)(address)) - PER_MEM_BASE) * 32	\
			+ (bitNum) * 4))

    /*! Shortcut to directly access an I/O-bit. */
#define IO_Bit(regName, bitNum)	*IO_BIT_ADDR(&regName, bitNum)

    /*! Macro to address a single bit in an SRAM variable in an atomic manner.
     * @param address   Address of the variable in SRAM.
     * @param bitNum    Bit number within this variable.
     */
#define SRAM_BIT_ADDR(address, bitNum)					\
	((__IO uint32_t *) (BITBAND_RAM_BASE				\
			+ (((uint32_t)(address)) - RAM_MEM_BASE) * 32	\
			+ (bitNum) * 4))

    /*! Shortcut to directly access a bit in a variable. */
#define Bit(varName, bitNum)	*SRAM_BIT_ADDR(&varName, bitNum)

/*=========================== Typedefs and Structs ===========================*/

/*!@brief Structure to hold Project Information */
typedef struct
{
    char const  ID[12];
    char const  Date[16];
    char const  Time[10];
    char const  Version[16];
} PRJ_INFO;


/*!@brief Enumeration of Alarm Identifiers
 *
 * This is the list of Alarm IDs used by this application.  They are used to
 * identify a particular alarm time entry via the <b>alarmNum</b> parameter
 * when calling alarm functions, e.g. AlarmSet().
 */
typedef enum
{
    END_ALARM_ID
} ALARM_ID;


/*!@brief Enumeration of the EM1 Modules
 *
 * This is the list of Software Modules that require EM1 to work, i.e. they
 * will not work in EM2 because clocks, etc. would be disabled.  These enums
 * are used to set/clear the appropriate bit in the @ref g_EM1_ModuleMask.
 */
typedef enum
{
    EM1_MOD_SERVO,	//!<  0: Servo timers require the 32MHz HF clock
    END_EM1_MODULES
} EM1_MODULES;

/*======================== External Data and Routines ========================*/

extern volatile bool	 g_flgIRQ;		// Flag: Interrupt occurred
extern volatile uint16_t g_EM1_ModuleMask;	// Modules that require EM1


#endif /* __INC_config_h */

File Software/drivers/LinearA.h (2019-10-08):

/***************************************************************************//**
 * @file
 * @brief	Header file of module LinearA.c
 * @author	Ralf Gerhauser
 * @version	2017-10-14
 ****************************************************************************//*
Revision History:
2017-10-14,rage	Completed version 2.0.
2017-09-09,rage	Initial version, based on "Servo.h".
*/

#ifndef __INC_LinearA_h
#define __INC_LinearA_h

/*=============================== Header Files ===============================*/

#include <stdio.h>
#include <stdbool.h>
#include "em_device.h"
#include "em_gpio.h"
#include "config.h"		// include project configuration parameters
#include "Keys.h"

/*=============================== Definitions ================================*/

/*!@brief Definitions for the PA3_SERVO_ENABLE signal (DC/DC converter) */
#define SERVO_ENABLE_PORT	gpioPortA
#define SERVO_ENABLE_PIN	3
#define SERVO_ENABLE   IO_Bit(GPIO->P[SERVO_ENABLE_PORT].DOUT, SERVO_ENABLE_PIN)

/*!@brief Definitions for the PE10_EN_LINEAR signal (low-active) */
#define EN_LINEAR_PORT		gpioPortE
#define EN_LINEAR_PIN		10
#define EN_LINEAR	IO_Bit(GPIO->P[EN_LINEAR_PORT].DOUT, EN_LINEAR_PIN)

/*!@brief Definitions for the PE11_DIR_LINEAR signal */
#define DIR_LINEAR_PORT		gpioPortE
#define DIR_LINEAR_PIN		11
#define DIR_LINEAR	IO_Bit(GPIO->P[DIR_LINEAR_PORT].DOUT, DIR_LINEAR_PIN)
#define DIR_LINEAR_POS_INC	1	// logical state for position increment
#define DIR_LINEAR_POS_DEC	0	// logical state for position decrement

/*!@brief Definitions for the PE12_ASTR_LINEAR signal (low-active) */
#define ASTR_LINEAR_PORT	gpioPortE
#define ASTR_LINEAR_PIN		12
#define ASTR_LINEAR	IO_Bit(GPIO->P[ASTR_LINEAR_PORT].DOUT, ASTR_LINEAR_PIN)

/*!@brief Definitions for the position zero detection input (low-active) */
#define POS_ZERO_DETECT_PORT	gpioPortA
#define POS_ZERO_DETECT_PIN	5
#define POS_ZERO_DETECT IO_Bit(GPIO->P[POS_ZERO_DETECT_PORT].DIN, POS_ZERO_DETECT_PIN)

/*!@brief Stepper pulses per [mm].
 * According to the data sheet of the L2018S0604 stepper motor, it moves
 * 0.005 mm/step, i.e. 200 steps/mm.  Because the SMC-11 controller is
 * configured for microstep mode, this means 16 pulses per step, there are
 * 3200 pulses/mm required.
 */
#define PULSES_PER_MM			(16L * 200L)

/*!@brief Total distance to move in [mm]. */
//#define TOTAL_DIST_IN_MM		100L	// 10cm
#define TOTAL_DIST_IN_MM		50L	// 5cm


/*!@brief Distance to speed up in [mm]. */
#define SPEED_UP_DIST_IN_MM		10L	// 1cm

/*!@brief Distance to slow down in [mm]. */
#define SLOW_DOWN_DIST_IN_MM		10L	// 1cm

/*!@brief Number of [mm] to move per key hit during setup of end-points. */
#define SETUP_DELTA_POS_MM		1 / 5	// DO NOT USE BRACKETS!

/*!@brief Minimum speed, used to reach final target position. */
#define STEPPER_MIN_SPEED		100L

/*!@brief Speed during setup process of the end-points. */
#define SETUP_SPEED			150L

/*!@brief Speed during calibration, i.e. reaching the physical end position. */
#define CALIBRATION_SPEED		400L

/*!@brief Maximum allowed speed. */
#define STEPPER_MAX_SPEED		600L


/*!@brief Timeout in [s] to leave setup mode when no key has been asserted */
#define KEY_INACTIVITY_TIMEOUT		30	// 30s

/*!@brief Here follows the definition of the two trigger inputs and their
 * related hardware configuration.  A falling edge triggers the movement of
 * the servo to the respective end position 1 or 2.
 */
#define TRIG_POS_2_PORT	gpioPortC
#define TRIG_POS_2_PIN	6

#define TRIG_POS_1_PORT	gpioPortC
#define TRIG_POS_1_PIN	7

/*!@brief Bit mask of all affected external interrupts (EXTIs). */
#define TRIG_EXTI_MASK	((1 << TRIG_POS_1_PIN) | (1 << TRIG_POS_2_PIN))

/*================================ Prototypes ================================*/

    /* Initialize servo hardware */
void	LinearInit(void);

    /* Key handler to setup and control the servo */
void	LinearKeyHdl(KEYCODE keycode);

    /* Handler for the two trigger inputs */
void	LinearTrigHdl(int extiNum, bool extiLvl, uint32_t timeStamp);


#endif /* __INC_LinearA_h */

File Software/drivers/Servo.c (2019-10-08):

/***************************************************************************//**
 * @file
 * @brief	Servo Control
 * @author	Ralf Gerhauser
 * @version	2016-10-05
 *
 * This module provides the functionality to control a servo.  In detail, this
 * includes:
 * - Initialization and configuration of the required devices.
 * - PWM signal generation to control the servo position.
 * - A setup routine to adjust the end-points and speed of the servo.
 * - EEPROM-like storage to save the configuration.
 *
 * The firmware supports soft-start, i.e. the servo speed will be ramped-up
 * during the start phase.
 *
 * @warning
 * There must be a stable PWM signal before powering the servo, otherwise
 * the servo will start moving to a wrong position.
 *
 ****************************************************************************//*
Revision History:
2016-10-05,rage	Completed version 1.0, added support for external inputs.
2016-09-09,rage	Initial version.
*/

/*=============================== Header Files ===============================*/

#include <stdio.h>
#include "config.h"	// include project configuration parameters

#if ! CFG_LINEAR_A  ||  DOXYGEN		// standard PWM servo

#include "AlarmClock.h"
#include "Servo.h"
#include "em_device.h"
#include "em_assert.h"
#include "em_cmu.h"
#include "em_int.h"
#include "em_prs.h"
#include "em_timer.h"
#include "eeprom_emulation.h"

/*=============================== Definitions ================================*/

/*!@brief Minimum and maximum servo speed, i.e. the step width per 20ms. */
#define SERVO_MIN_SPEED	1
#define SERVO_MAX_SPEED	256

/*!@brief Servo position (PWM value) where calibration starts. */
#define SERVO_START_POS	((SERVO_PWM_MIN_VALUE + SERVO_PWM_MAX_VALUE) / 2)

/*! Magic ID for EEPROM block */
#define MAGIC_ID	0x0815

/*=========================== Typedefs and Structs ===========================*/

/*!@brief Operating and Setup modes for the servo. */
typedef enum
{
    SERVO_MODE_OPERATIONAL,	//!< 0: Normal servo operating mode
    SERVO_MODE_SETUP_POS_1,	//!< 1: Setup mode: adjust first position
    SERVO_MODE_SETUP_POS_2,	//!< 2: Setup mode: adjust second position
    SERVO_MODE_SETUP_SPEED,	//!< 3: Setup mode: adjust speed
    END_SERVO_MODE		//!< End of servo mode definitions
} SERVO_MODE;

/*================================ Local Data ================================*/

    /*! Timer handle for key inactivity timer */
static TIM_HDL		l_thTimeout = NONE;

    /*! Flag shows if there are valid servo settings stored in flash. */
static volatile bool	l_ServoDataValid = false;

    /*! Actual servo mode */
static volatile SERVO_MODE l_ServoMode = SERVO_MODE_SETUP_POS_1;

    /*! Actual servo position (PWM value) */
static volatile int	l_ServoPos = SERVO_START_POS;

    /*! Servo end-position 1 */
static volatile int	l_ServoPos_1 = SERVO_START_POS;

    /*! Servo end-position 2 */
static volatile int	l_ServoPos_2 = SERVO_START_POS;

    /*! Servo speed, i.e. delta position per 20ms */
static volatile int	l_ServoSpeed = SERVO_PWM_DFLT_SPEED;

    /*! Servo direction during speed calibration mode */
static volatile bool	l_DirIncrease;

    /*! Servo enable flag: true means ON, false means OFF */
static volatile bool	l_ServoEnable;

    /*! Servo start time counter (soft start) when servo starts moving [%] */
static volatile int	l_ServoStartCnt;

    /*! Servo stopping time counter after position has been reached [20ms] */
static volatile int	l_ServoStopCnt = SERVO_STOPPING_TIME;

    /*! Define the non-volatile variables. */
static EE_Variable_TypeDef  magic, pos1, pos2, speed, chksum;


/*=========================== Forward Declarations ===========================*/

static void	ServoKeyTimeout (TIM_HDL hdl);
static void	ServoCtrlEnable(void);
static void	ServoCtrlDisable(void);
static bool	ReadServoParms(void);
static void	WriteServoParms(void);

/***************************************************************************//**
 *
 * @brief	Servo control initialization
 *
 * This routine must be called once to initialize all the devices required to
 * control a servo.  It also loads the servo configuration (end-points and
 * speed) from FLASH.
 *
 ******************************************************************************/
void	ServoInit (void)
{
#if 1	// RAGE: should be hardwired
    /* Always enable GND for the Servo via PA6_APP_SWITCH */
    GPIO_PinModeSet(gpioPortA, 6, gpioModePushPull, 1);
#endif
    /* PA3_SERVO_ENABLE, SERVO_VDD*/
    GPIO_PinModeSet(SERVO_ENABLE_PORT, SERVO_ENABLE_PIN, gpioModePushPull, 0);

    /*
     * Configure GPIOs for the trigger inputs.  The port pins must be
     * configured for input, and connected to the external interrupt (EXTI)
     * facility.  At this stage, the interrupts are not enabled, this is
     * done later by calling ExtIntInit().
     */
    GPIO_PinModeSet (TRIG_POS_1_PORT, TRIG_POS_1_PIN, gpioModeInputPull, 1);
    GPIO_IntConfig  (TRIG_POS_1_PORT, TRIG_POS_1_PIN, false, false, false);

    GPIO_PinModeSet (TRIG_POS_2_PORT, TRIG_POS_2_PIN, gpioModeInputPull, 1);
    GPIO_IntConfig  (TRIG_POS_2_PORT, TRIG_POS_2_PIN, false, false, false);

    /* Create inactivity timer */
    l_thTimeout = sTimerCreate (ServoKeyTimeout);

    /* Enables the flash controller for writing. */
    MSC_Init();

    /* Initialize the eeprom emulator using 3 pages. */
    if ( !EE_Init(3) )
    {
	/* If the initialization fails we have to take some measure
	 * to obtain a valid set of pages. In this example we simply
	 * format the pages
	 */
	EE_Format(3);
    }

    /* Declare variables (virtual addresses) */
    EE_DeclareVariable(&magic);
    EE_DeclareVariable(&pos1);
    EE_DeclareVariable(&pos2);
    EE_DeclareVariable(&speed);
    EE_DeclareVariable(&chksum);

    /* Get servo end-points from flash */
    if (ReadServoParms())
    {
	l_ServoDataValid = true;
	l_ServoPos = l_ServoPos_1;
	l_ServoMode = SERVO_MODE_OPERATIONAL;
    }

    /*
     * We use timer 1 for the 50Hz time base (servo requires PWM pulse every
     * 20ms) and timer 2 for the pulse generation.  This is, timer 2 run in
     * one-shot mode and is triggered (reloaded and started) by timer 1.
     * CC0 (capture/compare channel 0) of timer 2 is routed to PC8.
     */
    /* Enable clock for GPIO module should already be done) */
    CMU_ClockEnable(cmuClock_GPIO, true);
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

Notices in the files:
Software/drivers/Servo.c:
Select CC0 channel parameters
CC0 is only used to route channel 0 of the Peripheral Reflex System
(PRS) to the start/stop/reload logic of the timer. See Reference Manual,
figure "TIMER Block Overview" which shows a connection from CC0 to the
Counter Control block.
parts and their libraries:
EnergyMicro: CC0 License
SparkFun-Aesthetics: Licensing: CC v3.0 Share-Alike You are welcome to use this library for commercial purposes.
